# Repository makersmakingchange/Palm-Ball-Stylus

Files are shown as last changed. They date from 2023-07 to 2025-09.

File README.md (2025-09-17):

# Palm Ball Stylus
The Palm Ball Stylus is intended for users who cannot use traditional stylus pens for a variety of reasons. Instead of a traditional pen style stylus, it ends in a large ball that requires much less strength and dexterity to grip. The device uses a length of wire and conductive foam to allow the user to interact with the capacitive touchscreen. 

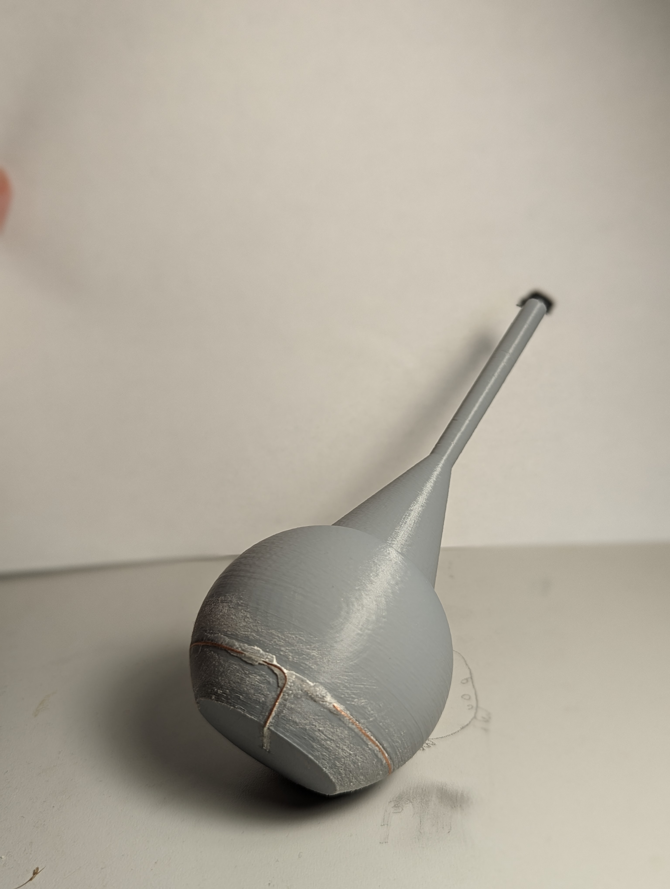
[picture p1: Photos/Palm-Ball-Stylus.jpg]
Picture of Palm Ball Stylus.


## More info at
- [Makers Making Change Project Page](https://makersmakingchange.com/project/palm-ball-stylus/)

## How to Obtain a Palm Ball Stylus
### 1. Do it Yourself (DIY) or Do it Together (DIT)

This is an open-source assistive technology, so anyone is free to build it. All of the files and instructions required to build the Palm Ball Stylus are contained within this repository. Refer to the Maker Checklist below.

### 2. Request a build of this device

If you would like to obtain a Palm Ball Stylus, you may submit a build request through the [MMC Library Page](https://makersmakingchange.com/project/palm-ball-stylus/). The requestor is responsible for the cost of materials and any shipping.

### 3. How to build this device for someone else

If you have the skills and equipment to build this device, and would like to donate your time to create the switch for someone who needs it, visit the [MMC Maker Wanted](https://makersmakingchange.com/maker-wanted/) section.

## Getting Started

### 1. Read the Makers Checklist

The Makers Checklist provides an overview of how to build, and test the device.

### 2. Order the Off-The-Shelf Components

The [Bill of Materials](/Documentation/Palm_Ball_Stylus_BOM_V1.0.xlsx) lists all of the parts and components required to build the Palm Ball Stylus. The off-the-shelf components are also online or may be available in smaller quantities at your local hardware store or dollar store.

### 3. Print the 3D Printable components

Print the components

All of the individual print files can be in the [/Build_Files/3D_Printing_Files](/Build_Files/3D_Printing_Files/) folder.

### 4. Assemble the Palm Ball Stylus

Reference the [Assembly Guide](/Documentation/Palm_Ball_Stylus_Assembly_Guide_V1.0.pdf) for the tools and steps required to build each portion.

## Files
### Documentation
| Document             | Version | Link |
|----------------------|---------|------|
| Design Rationale     | 1.0     | [Palm_Ball_Stylus_Design_Rationale](/Documentation/Palm_Ball_Stylus_Design_Rationale_V1.0.pdf)     |
| Maker Checklist      | 1.0     | [Palm_Ball_Stylus_Maker_Checklist](/Documentation/Palm_Ball_Stylus_Maker_Checklist_V1.0.pdf)     |
| Bill of Materials    | 1.1     | [Palm_Ball_Stylus_Bill_of_Materials](/Documentation/Palm_Ball_Stylus_BOM_V1.1.xlsx)     |
| 3D Printing Guide    | 1.0     | [Palm_Ball_Stylus_3D_Printing_Guide](/Documentation/Palm_Ball_Stylus_3D_Printing_Guide_V1.0.pdf)     |
| Assembly Guide       | 1.1     | [Palm_Ball_Stylus_Assembly_Guide](/Documentation/Palm_Ball_Stylus_Assembly_Guide_V1.1.pdf)     |
| User Guide           | 1.0     | [Palm_Ball_Stylus_User_Guide](/Documentation/Palm_Ball_Stylus_User_Guide_V1.0.pdf)    |
| Changelog            | 1.1     | [Palm_Ball_Stylus_Changelog](/Documentation/Palm_Ball_Stylus_Changelog_V1.1.pdf)     |

### Design Files
 - [CAD Files](/Design_Files)

### Build Files
 - [3D Printing Files](/Build_Files/3D_Printing_Files)

## Attribution
Designers:
 - The original [Ball Stylus Rev 4](https://www.thingiverse.com/thing:1319883) design using conductive filament was created by [Michael Papp / accesswoodworx](https://www.thingiverse.com/accesswoodworx) and licensed under the Creative Commons - Attribution license [(CC-BY)](https://creativecommons.org/licenses/by/4.0/).
 - Updated design and documentation by Neil Squire Society/Makers Making Change

## License
Everything needed or used to design, make, test, or prepare the Palm Ball Stylus is licensed under the [Attribution-NonCommercial-ShareAlike 4.0 ](https://creativecommons.org/licenses/by-nc-sa/4.0/).

Accompanying material such as instruction manuals, videos, and other copyrightable works that are useful but not necessary to design, make, test, or prepare the Palm Ball Stylus are published under a Creative Commons Attribution-ShareAlike 4.0 license https://creativecommons.org/licenses/by-sa/4.0/ (CC BY-SA 4.0).

----

<!-- ABOUT MMC START -->
## About Makers Making Change
[Makers Making Change Logo](https://www.makersmakingchange.com/)

Makers Making Change is a program of [Neil Squire](https://www.neilsquire.ca/), a Canadian non-profit that uses technology, knowledge, and passion to empower people with disabilities.

Makers Making Change leverages the capacity of community based Makers, Disability Professionals and Volunteers to develop and deliver affordable Open Source Assistive Technologies.

 - Website: [www.MakersMakingChange.com](https://www.makersmakingchange.com/)
 - GitHub: [makersmakingchange](https://github.com/makersmakingchange)
 - Bluesky: [@makersmakingchange.bsky.social](https://bsky.app/profile/makersmakingchange.bsky.social)
 - Instagram: [@makersmakingchange](https://www.instagram.com/makersmakingchange)
 - Facebook: [makersmakechange](https://www.facebook.com/makersmakechange)
 - LinkedIn: [Neil Squire Society](https://www.linkedin.com/company/neil-squire-society/)
 - Thingiverse: [makersmakingchange](https://www.thingiverse.com/makersmakingchange/about)
 - Printables: [MakersMakingChange](https://www.printables.com/@MakersMakingChange)

### Contact Us
For technical questions, to get involved, or to share your experience we encourage you to [visit our website](https://www.makersmakingchange.com/) or [contact us](https://www.makersmakingchange.com/s/contact).
<!-- ABOUT MMC END -->

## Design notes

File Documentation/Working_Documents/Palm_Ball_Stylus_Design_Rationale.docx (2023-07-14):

# Introduction

This device is intended for users that cannot use traditional stylus pens for a variety of reasons. Instead of a traditional pen style stylus, it ends in a large ball that requires much less strength and dexterity to grip. The device uses a length of wire and conductive foam to allow the user to interact with the capacitive touchscreen.

# Research

No other commercial or DIY palm ball style styluses were found on the market.

# Requirements

## Goals

G01 | Create a conductive stylus device with a palm ball grip

## Functional Requirements

F01 | Device must have a ball grip
F02 | Device must work with phone style touch screens

## Non-Functional Requirements

NF01 | Device must be low cost

## Constraints

C01 | Device must be 3D printable

# Testing

The original OpenSCAD model was printed first to get a feel for the device. Since it was meant to be printed in conductive filament, it did not work to operate a screen. A modified version was created in Fusion 360 that incorporated a channel for a wire to conduct from the user to the touchscreen. This design was printed and found to work well.

# Opportunities for Improvement

In future iterations, more wire channels could be added to allow more rings of wire to be added, so the ball could be gripped in more positions without risk of breaking contact with the wire.

© 2023 by Neil Squire. This work is licensed under the CC BY SA 4.0 License: http://creativecommons.org/licenses/by-sa/4.0 Files available at https://makersmakingchange.com/project/palm-ball-stylus/ Page 1 of 1

V1.0 | July 2023 Palm Ball Stylus Design Rationale

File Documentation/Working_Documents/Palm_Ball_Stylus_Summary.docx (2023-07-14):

# Title

Palm Ball Stylus

## Subtitle

This device is intended for users that cannot use traditional stylus pens for a variety of reasons.

## Device Details

### Overview

This device is intended for users that cannot use traditional stylus pens for a variety of reasons. Instead of a traditional pen style stylus, it ends in a large ball that requires much less strength and dexterity to grip. The device uses a length of wire and conductive foam to allow the user to interact with the capacitive touchscreen.

### Usage

To use the device, hold the ball with the stylus end facing away from the palm. For the device to work, the user must maintain skin contact with the wire along the side of the ball. The device can then be used as a traditional stylus.

### Cost

<$5

### Build Instructions

See detailed build instructions in Assembly Guide.

#### Skills Required

- 3D printing

#### Time Required

4h 28min

10 min

#### Tools

- Wire Strippers
- Superglue
- Sandpaper

#### Components

- Palm Ball Stylus
- Breadboard wire
- Conductive foam

#### 3D Printing

- Palm_Ball_Stylus.stl

### Attribution

Initial design by Michael Papp (https://www.thingiverse.com/accesswoodworx/designs) on Thingiverse (https://www.thingiverse.com/thing:1319883)

© 2023 by Neil Squire. This work is licensed under the CC BY SA 4.0 License: http://creativecommons.org/licenses/by-sa/4.0 Files available at https://makersmakingchange.com/project/palm-ball-stylus/ Page 1 of 1

V1.0 | July 2023 Palm Ball Stylus Summary

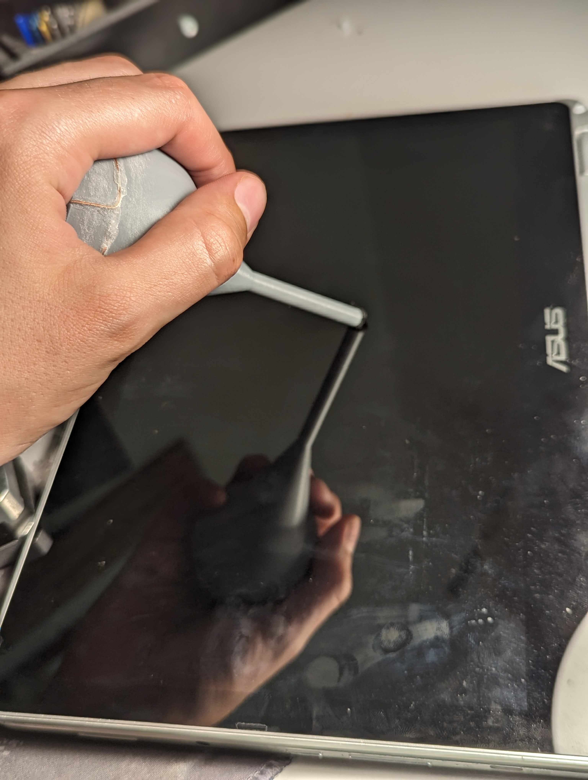
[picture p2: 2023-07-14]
Photos/PXL_20230704_202049578.PORTRAIT.jpg

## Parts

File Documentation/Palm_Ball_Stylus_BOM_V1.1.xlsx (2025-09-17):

Device: Palm Ball Stylus |  | Total Cost | Total Print time (hr) | Total filament (g)
Version: V1.0 | Date Created: 7/04/2023 | $2.32 | 0.00 | 42
Commercial Parts:
Part type (Electrical. Mechanical, Sanitization, ect) | Part Name | Quantity Needed | Pkg Quantity | Price per package | Price per Inch | Price for qty needed | Link
Mechanical | Solid core wire | 1 | 1 | $0.79 | $0.79 | $0.79 | https://www.digikey.ca/en/products/detail/cnc-tech/1007-22-1-2000-001-1-TD/17799213
Mechanical | Conductive Foam | 0.125 | 6 | $22.96 | $3.83 | $0.48 | https://www.amazon.ca/Scotch-Brite-Non-Scratch-Scrub-Sponge-6-Sponges/dp/B0043P0IAK
3D Printed Parts ESTIMATED PRICING USING 1KG ROLL COST: | $25.00
Part | Description | Quantity Needed | TOTAL Mass (g) | Estimated Price | Print Time (Min) | Link
Palm_Ball_Stylus | Main part body | 1 | 42 | $1.05
 |  |  |  | $0.00
 |  |  |  | $0.00
 |  |  |  | $0.00
 |  |  |  | $0.00
 |  |  | Total Print Cost: | $1.05
Tools for Assembly
Wire strippers
Alternatives (if there are other sources for some parts link them below)
Part and description | Link

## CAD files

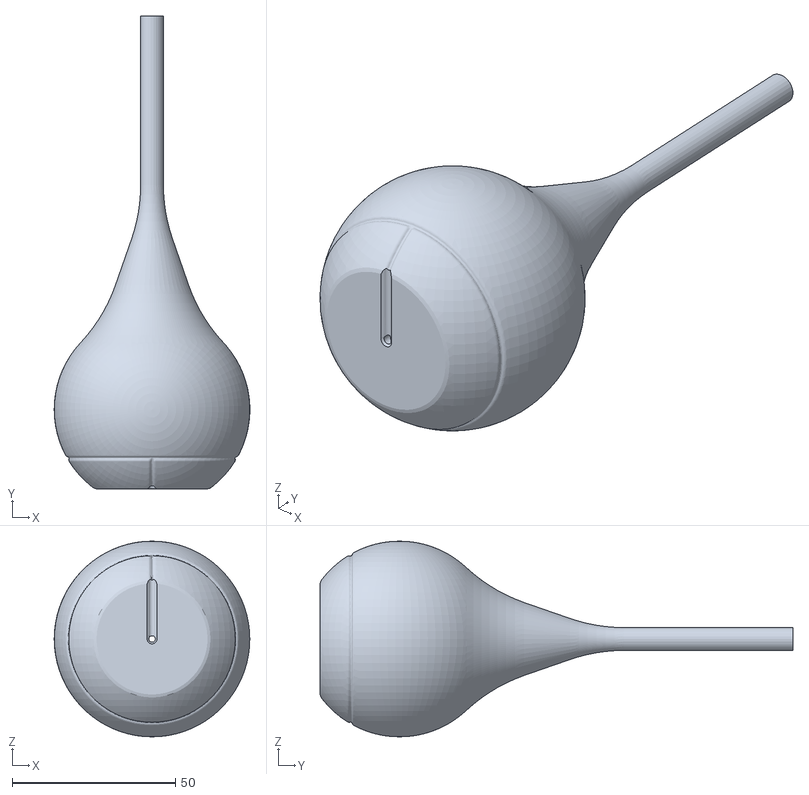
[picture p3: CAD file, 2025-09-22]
Build_Files/3D_Printing_Files/Palm_Ball_Stylus.stl
60.0 x 145.0 x 60.0

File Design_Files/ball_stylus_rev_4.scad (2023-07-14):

// Ball Diameter
ball_d = 60;  // [20:90]
// Stylus Length
stylus = 96;  // [20:230]
// Surface Smoothing
smooth = 30;  // [30:100]

$fn = smooth;
ball = ball_d/2;
union()
{
cylinder (h=stylus/3, r1=ball*sin(acos((ball-5)/ball)), r2=3.5);
difference()
{
translate([0,0,-ball+5])
sphere(ball);
translate([-ball, -ball, -ball*4+10])
cube(ball*2);
}
difference()
{
cylinder (h=stylus, r1=3.5, r2=3.5);
translate([0,0,stylus-9])
cylinder (h=9, r1=2.5, r2=2.5);
}
}

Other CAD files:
Design_Files/Palm Ball Stylus.f3d

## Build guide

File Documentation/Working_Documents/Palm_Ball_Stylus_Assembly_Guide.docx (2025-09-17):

# Required Components

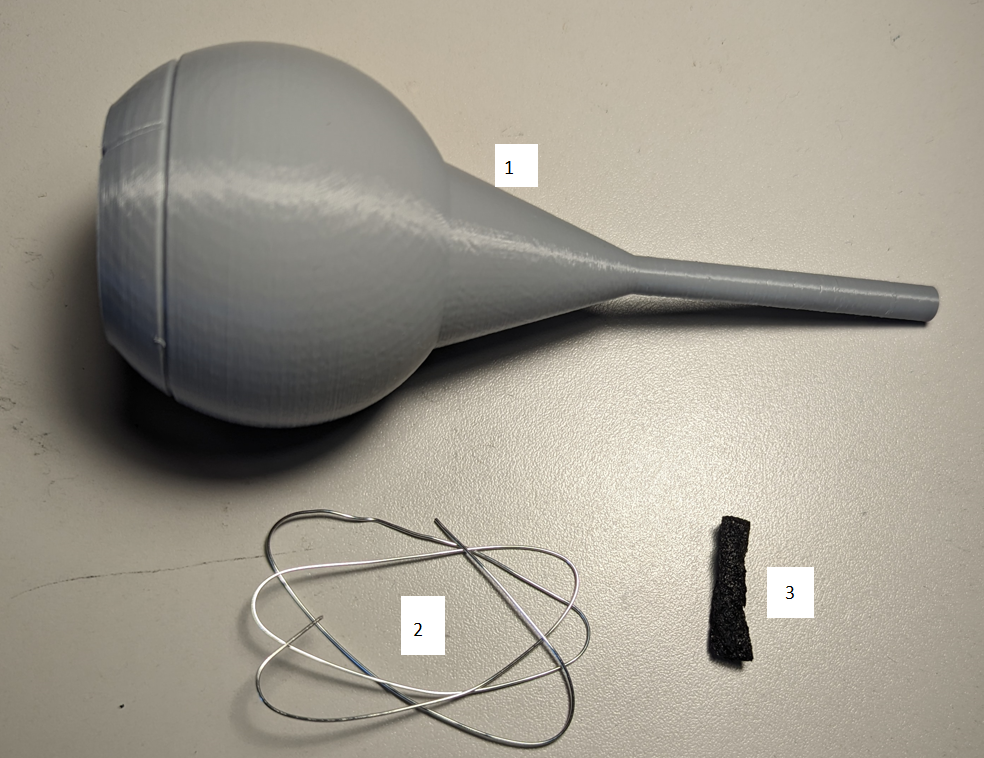
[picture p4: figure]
Labeled photo of the three components used to construct the Palm Ball Stylus

| BOM 1. Palm_Stylus 2. 22 AWG Breadboard Wire 3. Conductive Foam (The type ICs chips come shipped in, or a chunk of Scotch-Brite® Non-Scratch Scrub Sponge with the scrubby part cut off)

# Required Tools

- Wire strippers
- Superglue
- Sandpaper

# Required Personal Protective Equipment (PPE)

- Safety glasses

# Assembly Instructions

## Step 1

After 3D printing the stylus, take a roughly eight-inch piece of solid (not stranded) 22 AWG breadboard wire and remove the insulation from the entire piece. Run one end of the wire up through the bottom of the stylus until it emerges in the cavity at the end of the stylus, but not far enough to stick out past the end. Use superglue to secure the wire at the bottom of the stylus. Do not use solder as a wire, it can contain lead and should not be used in constant contact with the skin. Following the groove along the ball, run the remainder of the wire across the base, up the side of the ball, and around the circumference of the ball. Secure it in place with superglue. If the glue is taking overly long to dry, baking soda can be used as an accelerant to instantly dry the glue.

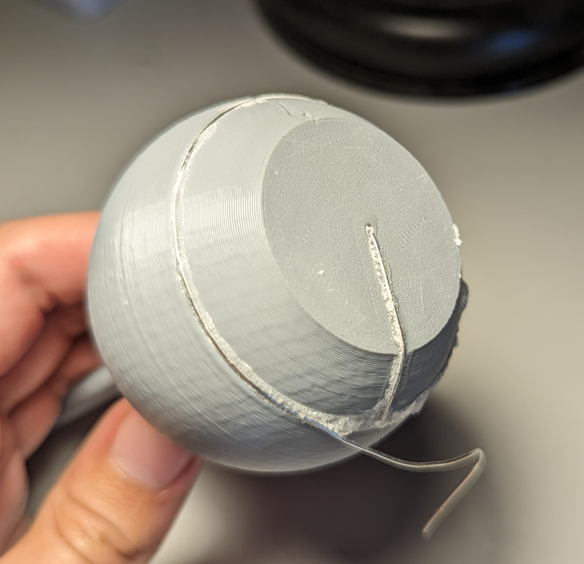
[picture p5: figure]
Photo showing the device with the wire glued in place, but before the wire has been sanded down. The excess wire is hanging off the ball and has not been trimmed yet.

## Step 2

After the glue dries, lightly sand the wire to expose the wire.

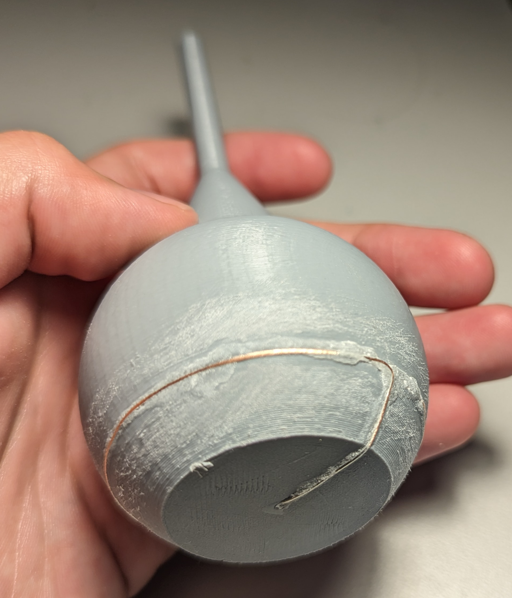
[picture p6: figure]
Angle one of the device with the wire sanded down
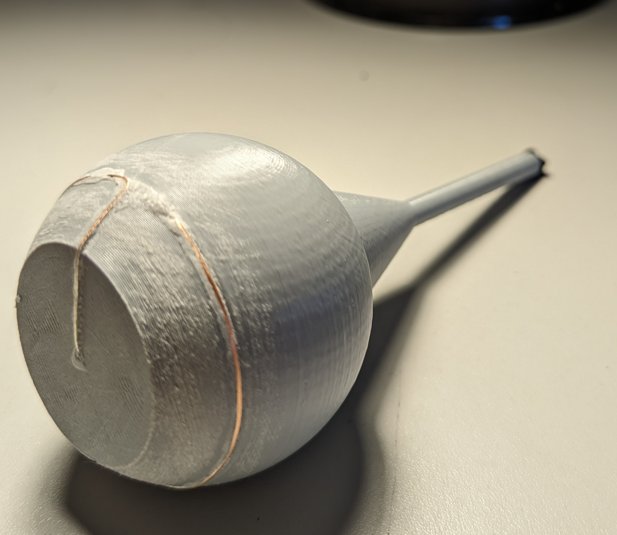
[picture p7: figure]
Angle two of the device with the wire sanded down

## Step 3

Finally, cut a length of the conductive foam, and stuff it in the cavity at the tip of the stylus. Trim any excess so that roughly a quarter of an inch sticks out, then remove the foam, add some superglue to the inside of the cavity, then put the foam back in. Ensure that the wire contacts the foam. After the glue dries, trim the foam to the desired tip shape.

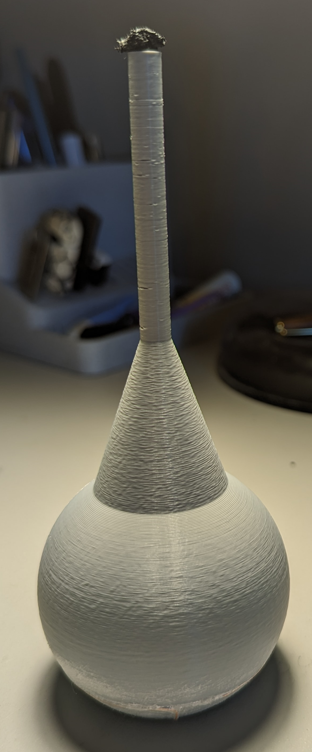
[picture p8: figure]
Photo showing the finished, assembled device

© 2025 by Neil Squire. This work is licensed under the CC BY SA 4.0 License: http://creativecommons.org/licenses/by-sa/4.0 Files available athttps://makersmakingchange.com/project/palm-ball-stylus/ Page 1 of 1

V1.1 | Sept 2025 Palm Ball Stylus Assembly Guide

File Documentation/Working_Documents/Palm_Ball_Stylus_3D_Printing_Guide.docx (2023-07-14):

# 3D Printing Summary

Metrics
Total Print Time (min) | 268
Total Number of Components | 1
Typical Total Mass (g) | 42
Typical Number of Print Setups | 1

# 3D Printing Settings

Print File Name | Qty | Total Print Time (hr:min) | Mass (g) | Infill (%) | Support(Y/N) | Layer Height/ Nozzle Diameter(mm) | Notes (orientation, special settings, etc.)
Palm_Ball_Stylus.stl | 1 | 4:28 | 42 | 20 | N | 0.2/0.4 | - Print in orientation given in STL

# Customization Options

- Device can be printed in any colour the user desires.
- Conductive PLA can be used to eliminate the need for the wire
- The diameter of the ball and length of the stylus can be edited in the fusion file

# Post-Processing

- No post processing is required

# Examples of Quality Prints

Photos of Palm_Ball_Stylus.stl

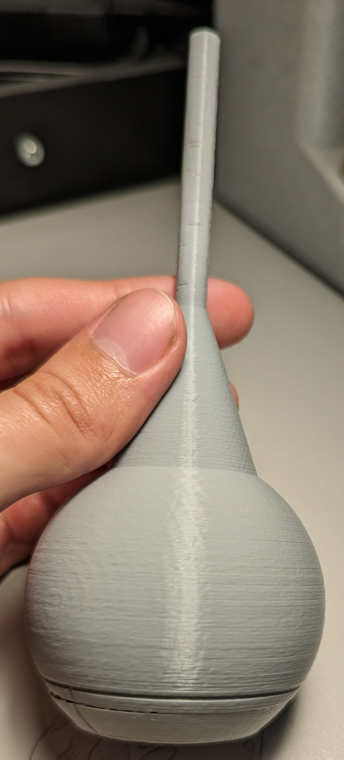
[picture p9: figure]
palm ball stylus stl

© 2023 by Neil Squire. This work is licensed under the CC BY SA 4.0 License: http://creativecommons.org/licenses/by-sa/4.0 Files available at https://makersmakingchange.com/project/palm-ball-stylus/ Page 1 of 2

V1.0 | July 2023 Palm Ball Stylus 3D Printing Guide

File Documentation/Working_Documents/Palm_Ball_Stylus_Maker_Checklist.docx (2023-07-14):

# Maker To Do List

- Read through the Assembly Guide to become familiar with required components, tools, supplies, and safety gear and overall assembly steps.
- Talk to User about customization options (e.g., color, any special requests, etc.)
- Order hardware components
- Gather tools, supplies, and safety equipment.
- Assemble the device
- Test device
- Print “User Quick Guide”

# Items to Give to User

- Assembled, tested device
- “User Quick Guide”

© 2023 by Neil Squire. This work is licensed under the CC BY SA 4.0 License: http://creativecommons.org/licenses/by-sa/4.0 Files available at https://makersmakingchange.com/project/palm-ball-stylus/ Page 1 of 1

V1.0 | July 2023 Palm Ball Stylus Maker Checklist

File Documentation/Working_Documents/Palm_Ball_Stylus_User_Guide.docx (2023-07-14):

## Introduction

This device is intended for users that cannot use traditional stylus pens for a variety of reasons. Instead of a traditional pen style stylus, it ends in a large ball that requires much less strength and dexterity to grip. The device uses a length of wire and conductive foam to allow the user to interact with the capacitive touchscreen.

## Features

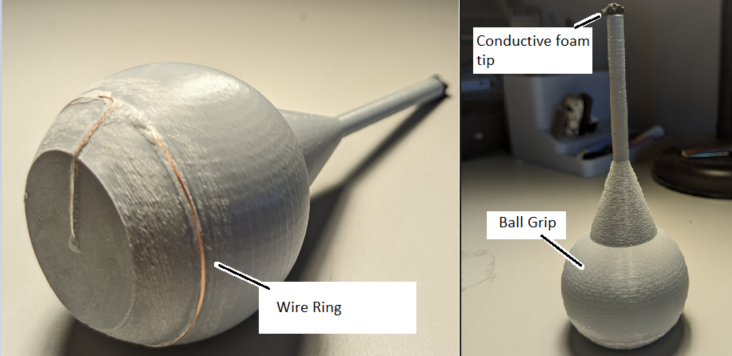
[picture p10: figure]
A labeled diagram of the device showing the ball grip, wire ring, and conductive foam tip.

## Usage

To use the device, hold the ball with the foam stylus end facing away from the palm. For the device to work, the user must maintain skin contact with the wire along the side of the ball. The device can then be used as a traditional stylus with the foam touching the device screen.

## Compatibility

This device works with smartphones, or any other device that works with a similar capacitive style touchscreen.

## Specifications

The diameter of the ball is 60mm, and the total height is 145mm

The assembled device weighs 45 grams

## Cleaning

The device can be wiped clean with a damp cloth.

© 2023 by Neil Squire. This work is licensed under the CC BY SA 4.0 License: http://creativecommons.org/licenses/by-sa/4.0 Files available at https://makersmakingchange.com/project/palm-ball-stylus/ Page 2 of 3

V1.0 | July 2023 Palm Ball Stylus user Quick Guide

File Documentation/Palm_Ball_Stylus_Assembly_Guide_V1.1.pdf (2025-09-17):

V1.1 | Sept 2025

## Palm Ball Stylus

## ASSEMBLY GUIDE

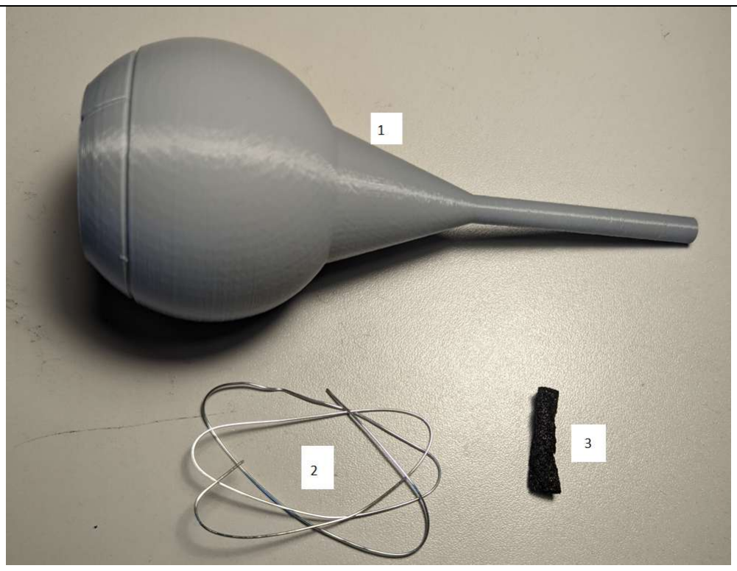
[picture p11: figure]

© 2025 by Neil Squire.
This work is licensed under the CC BY SA 4.0 License: http://creativecommons.org/licenses/by-sa/4.0
Files available athttps://makersmakingchange.com/project/palm-ball-stylus/ | Page 1 of 4

### Required Components

BOM

### 1. Palm_Stylus

2. 22 AWG
Breadboard Wire

### 3. Conductive Foam

(The type ICs chips
come shipped in, or
a chunk of Scotch-Brite® Non-Scratch
Scrub Sponge with
the scrubby part
cut off)

### Required Tools

- Wire strippers
- Superglue
- Sandpaper

### Required Personal Protective Equipment (PPE)

- Safety glasses

## ASSEMBLY GUIDE

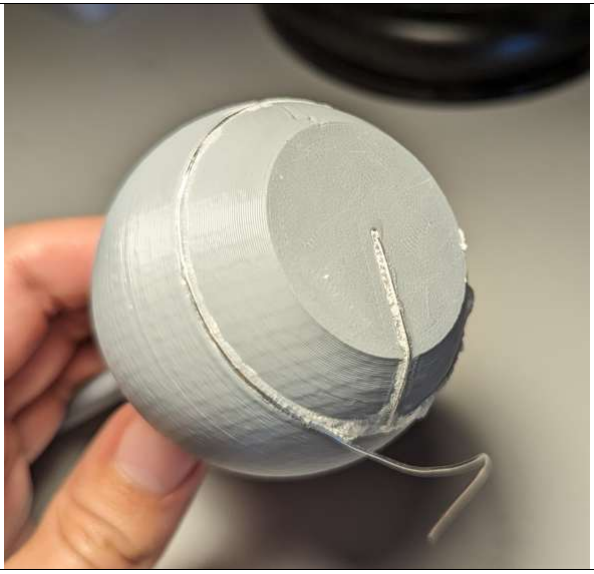
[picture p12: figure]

Files available athttps://makersmakingchange.com/project/palm-ball-stylus/ | Page 2 of 4

### Assembly Instructions

### Step 1

After 3D printing the stylus, take a roughly eight-inch piece of solid (not stranded) 22 AWG breadboard wire and remove the insulation from the entire piece. Run one end of the wire up through the bottom of the stylus until it emerges in the cavity at the end of the stylus, but not far enough to stick out past the end. Use superglue to secure the wire at the bottom of the stylus. Do not use solder as a wire, it can contain lead and should not be used in constant contact with the skin. Following the groove along the ball, run the remainder of the wire across the base, up the side of the ball, and around the circumference of the ball. Secure it in place with superglue. If the glue is taking overly long to dry, baking soda can be used as an accelerant to instantly dry the glue.

## ASSEMBLY GUIDE

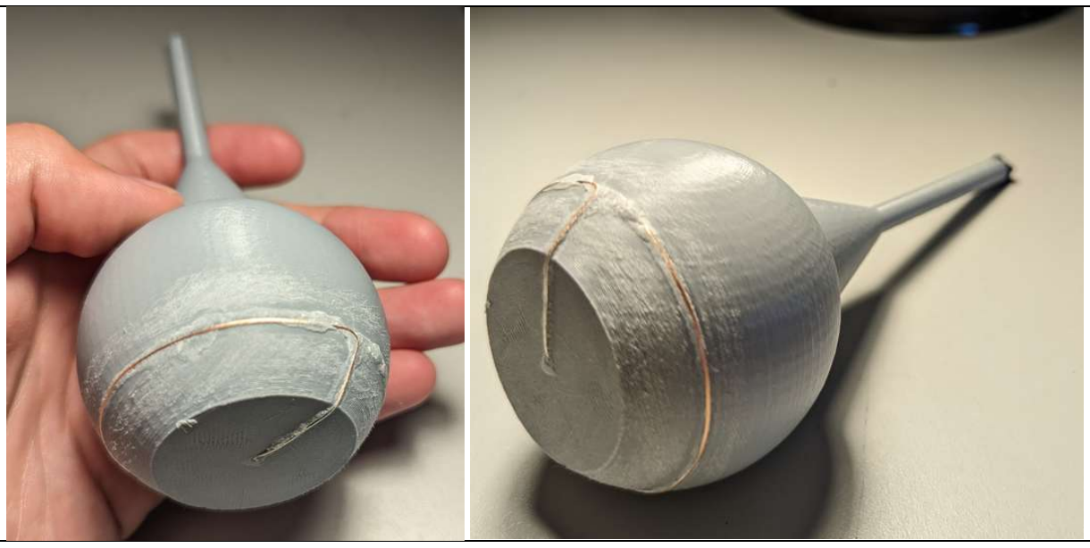
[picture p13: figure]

Files available athttps://makersmakingchange.com/project/palm-ball-stylus/ | Page 3 of 4

### Step 2

After the glue dries, lightly sand the wire to expose the wire.

## ASSEMBLY GUIDE

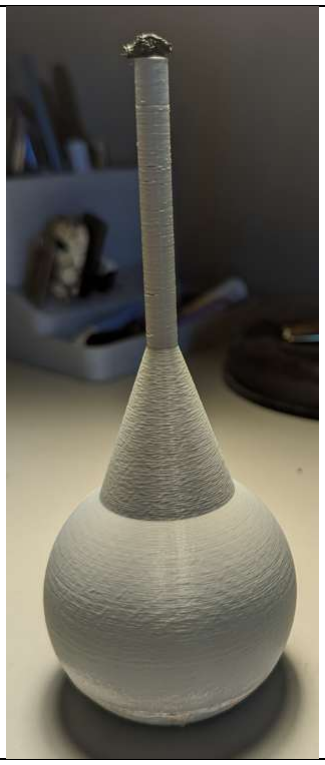
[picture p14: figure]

Files available athttps://makersmakingchange.com/project/palm-ball-stylus/ | Page 4 of 4

### Step 3

Finally, cut a length of the conductive foam, and stuff it in the cavity at the tip of the stylus. Trim any excess so that roughly a quarter of an inch sticks out, then remove the foam, add some superglue to the inside of the cavity, then put the foam back in. Ensure that the wire contacts the foam. After the glue dries, trim the foam to the desired tip shape.

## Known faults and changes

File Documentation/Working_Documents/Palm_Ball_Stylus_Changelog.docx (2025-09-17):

# Version 1.0 | 2023/07/04

- Initial design by Michael Papp (https://www.thingiverse.com/accesswoodworx/designs) on Thingiverse (https://www.thingiverse.com/thing:1319883)
- Documentation by Neil Squire Society/Makers Making Change

# Version 1.1 | 2025/09/17

- Changed wire in the BoM for one that can be bought by the foot.
- Updated Maker Guide to more clearly call out the correct wire to use.

© 2025 by Neil Squire. This work is licensed under the CC BY SA 4.0 License: http://creativecommons.org/licenses/by-sa/4.0 Files available athttps://makersmakingchange.com/project/palm-ball-stylus/ Page 1 of 1

V1.1 |Sept 2025 Palm Ball Stylus changelog

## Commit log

2023-07-14 Initial Commit
    Initial Commit
    [Palm Ball Stylus v1.f3d, Palm_Ball_Stylus.stl, Palm_Ball_Stylus_BOM.xlsx, Palm_Ball_Stylus_BOM_V1.0.xlsx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]
2025-09-17 Changed wire source and clarified assembly guide
    [Palm_Ball_Stylus_BOM_V1.0.xlsx, Palm_Ball_Stylus_BOM_V1.1.xlsx]
2025-09-22 Minor update to CAD files
    [Palm Ball Stylus v1.f3d, Palm Ball Stylus.f3d, Palm_Ball_Stylus.stl]
